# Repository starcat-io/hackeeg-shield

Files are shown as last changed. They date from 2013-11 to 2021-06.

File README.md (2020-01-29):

# HackEEG - ADS1299 Shield

This is an Arduino Due shield for the 
[TI ADS1299 EEG system-on-a-chip](http://www.ti.com/product/ads1299). This is a
system-on-a-chip that includes all commonly-required features for extracranial 
electroencephalogram (EEG) and electrocardiography (ECG) applications.

This board is currently available in the [HackEEG CrowdSupply crowdfunding campaign](https://www.crowdsupply.com/starcat/hackeeg/).
You can buy one or more of the boards by backing the campaign. Here's more about the [HackEEG product](http://starcat.io/hackeeg-shield).

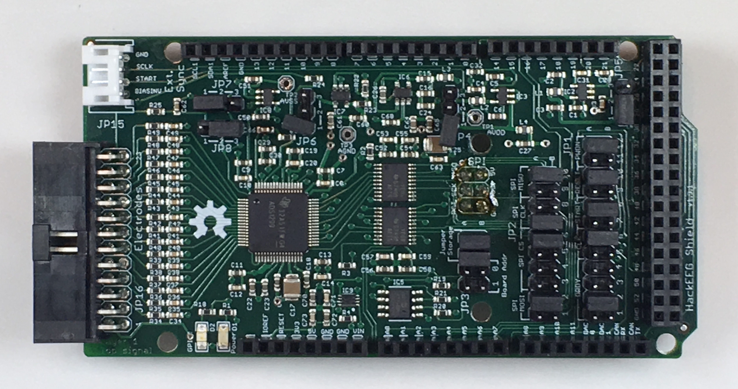
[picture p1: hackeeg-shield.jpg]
Picture of the HackEEG board


This board has been tested, works, and is in use in major research labs in the US and Europe. Design files for two connector boards
are included:

  * connector-8: this has 9 [DIN 42-802](https://en.wikipedia.org/wiki/EEG_DIN_connector) 
    medical electrode connectors (8 single-ended inputs, one ground)
  * connector-12: this has a 12-position screw-terminal connector with 8 single-ended inputs, ground, 
    analog power, digital power, and bias electrode.

I intend to eventually design a case and will post the files here when I do.

I can provide limited support for for individuals. Commercial support is available for corporations.

## Features

* Up to 4 shields can be stacked on one Arduino Due, for a total of 32 EEG channels
* DMA drivers can read and transfer 8 channels of 24-bit resolution data at 16,000 samples per second (Arduino Due only)
* SPI EEPROM for storing configuration data
* Jumpers for configuring most of the data and control lines to the Arduino
* 2 board-stacks can be daisy-chained and clock-synchronized to capture 64 EEG channels (this is experimental)
* Level shifters mean the board is compatible with both the [Arduindo Due](ihttps://store.arduino.cc/usa/due) and 
[Arduino Mega2560](https://store.arduino.cc/usa/mega-2560-r3).
* Single-ended and differential inputs are available on the electrode connector.

## Warning

When used with humans, mammals, or other higher animals, this board is meant to be used **only** in battery powered systems. It has no patient isolation circuitry.
Don't connect it, or any system it is connected to, to mains (wall or AC) power. **Use at your own risk.**

## Documentation

* [Connector Pinouts](https://github.com/starcat-io/hackeeg-shield/blob/master/docs/connectors.md)
* [Configuration Reference](https://github.com/starcat-io/hackeeg-shield/blob/master/docs/configuration.md)
* [Typical Configuration](https://github.com/starcat-io/hackeeg-shield/blob/master/docs/typical-configuration.md)

## Driver Software

The Arduino Due and Mega2560 driver software for this board can be found in the [hackeeg-driver-arduino](https://github.com/starcat-io/hackeeg-driver-arduino) repository.

## License

[CERN Open Hardware License v.1.2](http://ohwr.org/cernohl)

## Comments

If you have questions, comments, or improvements, I would love to know them!

cheers <br>
adam <br>
<br>
Adam Feuer <br>
adam@starcat.io<br>
[Starcat LLC](https://starcat.io)<br>
Seattle, WA, USA <br>

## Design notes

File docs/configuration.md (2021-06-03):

# HackEEG Configuration

These jumpers configure Arduino Due pins used on the HackEEG shield. For commonly-used settings, see [Typical Configuration](https://github.com/adamfeuer/hackeeg-shield/blob/master/docs/typical-configuration.md).

For ADS1299 pin definitions, refer to [ADS1299 datasheet](http://www.ti.com/lit/ds/symlink/ads1299.pdf).

For Arduino Due pin definitions, refer to the [Arduino Due pinout diagram](https://raw.githubusercontent.com/adamfeuer/hackeeg-shield/master/docs/arduino_due_pinout.png), the [Arduino Due reference](https://www.arduino.cc/en/Main/ArduinoBoardDue), and the [SAM3X8E datasheet](http://www.atmel.com/Images/Atmel-11057-32-bit-Cortex-M3-Microcontroller-SAM3X-SAM3A_Datasheet.pdf).

If you change these jumpers, you must also change the pin definitions in your driver files. For the ads129x_tools driver, this is in the file [adsCommand.h](https://github.com/adamfeuer/ADS129x-tools/blob/master/ads129x_driver/adsCommand.h)

## Jumper Diagram

This diagram shows the locations of all the configuration jumpers:

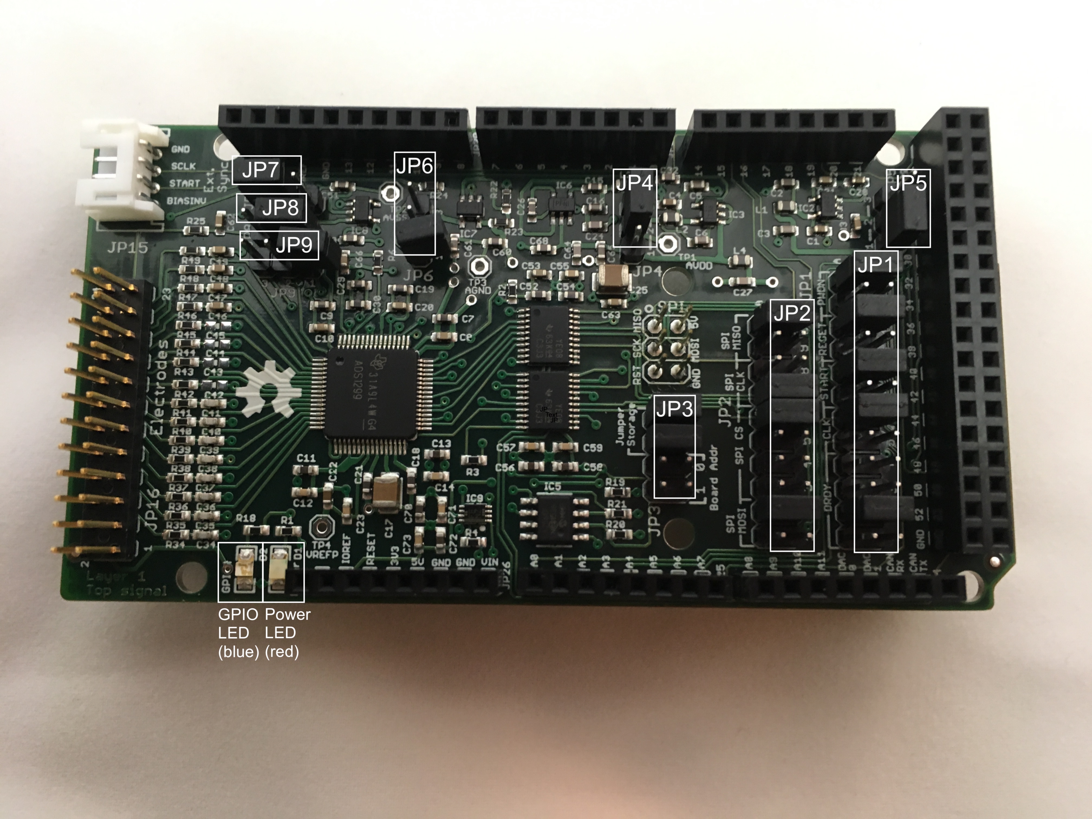
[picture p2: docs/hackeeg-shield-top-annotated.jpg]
Annotated picture of the HackEEG board showing jumper locations


## Digital Configuration Jumpers

### JP1 and JP2 – Board Connection

These pins select which ADS1299 pins are connected to which Arduino Due pins. Bridging one pair of jumpers connects the pins together. This enables a stack of shields to use different Arduino Due pins if needed, for instance to connect two HackEEG shields to the native SPI, and two to the USART1 SPI, or to use different Arduino Due PIO pins to control the ADS1299.

For each named signal, you must set exactly one jumper.
    
#### JP1 – Config0 – ADS1299 Control Configuration

| Signal      | Jumper #    | Arduino pin  |
|------------ |------------ | ------------ |
| `DRDY`      | 1           | D24          |
| `DRDY`      | 2           | D25          |
| `DRDY`      | 3           | D26          |
| `DRDY`      | 4           | D27          |
| `CLK`       | 5           | D30          |
| `CLK`       | 6           | D31          |
| `START`     | 7           | D61          |
| `START`     | 8           | D59          |
| `RESET`     | 9           | D46          |
| `RESET`     | 10          | D47          |
| `PWDN`      | 11          | D32          |
| `PWDN`      | 12          | D33          |

#### JP2 – Config1 – SPI Configuration

| Signal       | Port           | Jumper # | Arduino pin |
|------------  | -------------- | -------- |------------ |
| `SPI MOSI`   | Native         | 1        | SPI4        |
| `SPI MOSI`   | USART1         | 2        | D16         |
| `SPI CS`     | Chip Select    | 3        | D23         |
| `SPI CS`     | Chip Select    | 4        | D52         |
| `SPI CS`     | Chip Select    | 5        | D10         |
| `SPI CS`     | Chip Select    | 6        | D4          |
| `SPI SCL`    | Native         | 7        | SPI3        |
| `SPI SCL`    | USART1         | 8        | A0          |
| `SPI MISO`   | Native         | 9        | SPI1        |
| `SPI MISO`   | USART1         | 10       | D17         |

### Not configurable

These pins are hard-wired and cannot be configured.

| Signal      |Arduino pin        |
|------------ |------------------ |
| `CLKSEL`    | D48               |
| BOARD LED   | ADS1299 `GPIO4`   |

### JP3 – Board Address 

These pins set the 24AA256 I2S EEPROM address 0-3 in binary – they are not connected to Arduino Due pins. The pins are shared with the ADS1299 GPIO, and so can also used as the board address and read via the ADS1299. If not using them as jumpers, external devices can be connected to the header to provide access to the ADS1299 GPIO pins; this usage generally will conflict with using the I2S EEPROM.

| Jumper #   | Function          |
|----------- |------------------ |
| 0          | ADS1299 `GPIO0`   |
| 1          | ADS1299 `GPIO1`   |

## Analog Configuration Jumpers

### Instrumentation Power Supplies

These jumpers configure the instrumentation power supplies that supply the reference voltages for the ADS1299. You can set the ADS1299 to measure voltages in the 0–5V range (unipolar) or in the -2.5V – +2.5V range (bipolar). Bipolar is most commonly used for human or mammal subjects. You must bridge exactly one set of pins on each jumper.

#### JP 4

| Pins        | Function              |
|------------ |---------------------- |
| 1-2         | Sets `AVDD` to 5V     |
| 2-3         | Sets `AVDD` to 2.5V   |
 
#### JP 5

| Pins        | Function                  |
|------------ |-------------------------  |
| 1-2         | Sets `AVSS` to -2.5V      |
| 2-3         | Sets `AVDD` to `GROUND`   |

#### Common Settings

| Mode Name | ADS1299 Voltage Range    | JP4 Pins| JP5 Pins |
|---------- |------------------------- |---------|--------- |
| Unipolar  | 0–5V                     | 1-2     | 2-3      |
| Bipolar   | -2.5V – +2.5V            | 2-3     | 1-2      |

### Stimulus-Response Buffer (SRB)

#### JP6 – SRB1 - BIAS

| Pins              | Function                                                                              |
|---------------    |-------------------------------------------------------------------------------------- |
| 1-2               | Routes `SRB1` to `BIAS_ELEC` on the electrode connector via a 5K resistor             |
| 2-3               | Routes a noise source to `SRB1`                                                       |
| Unconnected       | Disconnects `BIAS` from `SRB1` – use in conjunction with JP7/JP8 `REF_ELEC` functions |

Setting pins 2-3 can be used to test channel noise performance. See section 8.3 of the [TI EEG Front-End Demonstration Kit manual](http://www.ti.com/lit/ug/slau443b/slau443b.pdf). In this mode, `BIAS_ELEC` and `REF_ELEC` on the electrode connector need to be connected with a cable, since there is no jumper to do so on the HackEEG board.

#### JP7 – SRB1–REF_ELEC 

| Pins          | Function                                                                 |
|------------   |------------------------------------------------------------------------- |
| 1-2           | Routes `SRB1` to `REF_ELEC` on the electrode connector via a 5K resistor |
| 2-3           | Routes `SRB2` to `SRB1` via an opamp                                     |

#### JP8 – SRB2–REF_ELEC 

| Pins          | Function                                                                          |
|------------   |---------------------------------------------------------------------------------- |
| 1-2           | Routes `REF_ELEC` on the electrode connector to the opamp input via a 5K resistor |
| 2-3           | Routes `SRB2` to the opamp input                                                  |

#### JP9 – BIASIN-BIASOUT-BIAS_ELEC 

| Pins          | Function                                                                       |
|------------   |------------------------------------------------------------------------------- |
| 1-2           | Routes `BIASOUT` to `BIAS_ELEC` on the electrode connector via a 5K resistor   |
| 2-3           | Routes `BIASOUT` to `BIASIN`                                                   |
| Unconnected   | Leaves `BIASOUT`, `BIASIN`, and `BIAS_ELEC` unconnected                        |

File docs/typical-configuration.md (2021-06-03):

# HackEEG Typical Configuration

The HackEEG comes from the factory configured this way and the drivers are set up to use it.

## Jumper Diagram

This diagram shows the locations of all the configuration jumpers:

Annotated picture of the HackEEG board showing jumper locations

## Digital Configuration Jumpers

### JP1 and JP2 – Board Connection
    
#### JP1 – Config0 – ADS1299 Control Configuration

| Signal      | Jumper #  | Arduino pin |
|------------ |---------- |------------ |
| `DRDY`      | 2         | D25         |
| `CLK`       | 6         | D31         |
| `START`     | 7         | D61         |
| `START`     | 8         | D59         |
| `RESET`     | 10        | D47         |
| `PWDN`      | 12        | D33         |

#### JP2 – Config1 – SPI Configuration

| Signal      | Port           |Jumper # | Arduino pin |
|------------ |--------------- |-------- |------------ |
| `SPI MOSI`  | Native         | 1       | SPI4        |
| `SPI CS`    | Chip Select    | 6       | D23         |
| `SPI SCL`   | Native         | 7       | SPI3        |
| `SPI MISO`  | Native         | 9       | SPI1        |

### Not configurable

These pins are hard-wired and cannot be configured.

| Signal      |Arduino pin        |
|------------ |------------------ |
| `CLKSEL`    | D48               |
| BOARD LED   | ADS1299 `GPIO4`   |

### JP3 – Board Address 

No jumpers set, so board address is 0.

## Analog Configuration Jumpers

### Instrumentation Power Supplies

The HackEEG comes configured in bipolar mode:

| Mode Name | ADS1299 Voltage Range    | JP4 Pins| JP5 Pins |
|---------- |------------------------- |---------|--------- |
| Bipolar   | -2.5V – +2.5V            | 2-3     | 1-2      |

#### JP 4

| Pins        | Function              |
|------------ |---------------------- |
| 2-3         | Sets `AVDD` to 2.5V   |
 
#### JP 5

| Pins        | Function                 |
|------------ |------------------------- |
| 1-2         | Sets `AVSS` to -2.5V     |

### Stimulus-Response Buffer (SRB)

#### JP6 – SRB1 - BIAS

| Pins           | Function                                                                              |
|--------------- |-------------------------------------------------------------------------------------- |
| Unconnected    | Disconnects `BIAS` from `SRB1` – use in conjunction with JP7/JP8 `REF_ELEC` functions |

#### JP7 – SRB2–REF_ELEC 

| Pins        | Function                                                             |
|------------ |--------------------------------------------------------------------- |
| Unconnected | Routes `REF_ELEC` on the electrode connector via a 5K resistor       |

#### JP8 – SRB1–REF_ELEC 

| Pins       | Function                                                                  |
|----------- | ------------------------------------------------------------------------- |
| 1-2        | Routes `SRB1` to `REF_ELEC` on the electrode connector via a 5K resistor  |

#### JP9 – BIASIN-BIASOUT-BIAS_ELEC 

| Pins          | Function                                                                       |
|------------   |------------------------------------------------------------------------------- |
| Unconnected   | Leaves `BIASOUT`, `BIASIN`, and `BIAS_ELEC` unconnected                        |

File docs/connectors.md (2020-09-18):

# HackEEG Connector Pinouts

## Electrode Connector

**JP16** is the electrode connector.

### Electrode connector pinout:

|Pin #	|Function						|
|-----	|-------------------------	|
|  1	|`DVDD`						|
|  2	|`AVDD`						|
|  3	|`BIASINV`					|
|  4	| Reserved for Future Use	|
|  5	|`AGND`						|
|  6	|`AGND`						|
|  7	|`IN1P`						|
|  8	|`IN1N`						|
|  9	|`IN2P`						|
| 10	|`IN2N`						|
| 11	|`IN3P`						|
| 12	|`IN3N`						|
| 13	|`IN4P`						|
| 14	|`IN4N`						|
| 15	|`IN5P`						|
| 16	|`IN5N`						|
| 17	|`IN6P`						|
| 18	|`IN6N`						|
| 19	|`IN7P`						|
| 20	|`IN7N`						|
| 21	|`IN8P`						|
| 22	|`IN8N`						|
| 23	|`REF_ELEC_CONN`				|
| 24	|`BIAS_ELEC_CONN`			|

Looking at the pins edge on (not from above), this is the pinout diagram:

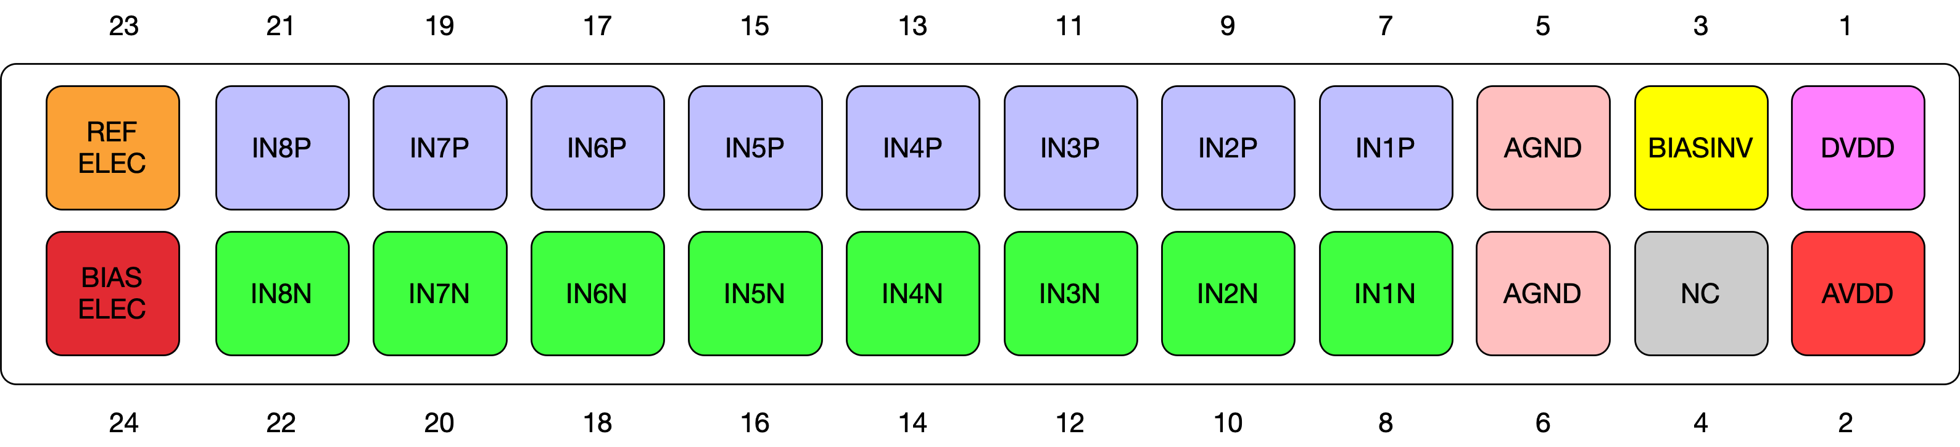
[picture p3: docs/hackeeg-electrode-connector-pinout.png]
HackEEG Electrode Connector pinout diagram


## External Sync connector

This connector is experimental, and not supported at this time. You can enable it using the various ADS1299 register settings.

### External Sync connector pinout

|Pin #	|Function			|
|-----	|---------------	|
| 1   	|`BIASINV`		|
| 2   	|`ADS_START`   	|
| 3  	|`ADS_SPI_CLK`	|
| 4  	|`AGND`   		|

## Checking the connector pinouts against the schematic

If you want to check the pinout, you can see the connectors on the schematic on sheet 2:

[HackEEG Shield schematic](https://github.com/adamfeuer/hackeeg-shield/blob/master/hackeeg-shield.pdf)

## Making cables

### Electrode Connector cables

**JP16** is the large, black male 24-pin shrouded electrode connector that is soldered on the board: [On Shore Technology 24-pin right angle male shrouded header](https://www.digikey.com/product-detail/en/on-shore-technology-inc/101-246/ED10537-ND)

This the mating female connector that I use to construct ribbon cables to connect the connector boards with the HackEEG shield:

[On Shore Technologies 	101-246 IDC socket connector for ribbon cable](https://www.digikey.com/product-detail/en/on-shore-technology-inc/101-246/ED10504-ND)

Here's the ribbon cable I used:

[24-conductor ribbon cable, 5 foot length](https://www.digikey.com/product-detail/en/3m/3365-24-300SF/MC24G-5-ND/)

You'll need a tool to crimp them, I used this one from Amazon:

[IDC crimp tool](https://www.amazon.com/gp/product/B007R2JEM4)

Alternatively, any 24-pin female header with receptacles on 0.1" centers should work if you want to use one and solder some wires to it.

### External Sync Connector cables

**JP15** is the small, white male 4-pin shrouded connector that is used for synchronizing the ADS1299 with another board.

This is the connector that is soldered on the board: [JST 4-pin Shrouded Male Header ](http://www.digikey.com/product-detail/en/S4B-PH-K-S(LF)(SN)/455-1721-ND/926628)

Here is the [Mating JST connector](http://www.digikey.com/product-detail/en/PHR-4/455-1164-ND/608606) and [Crimp Contact that fits the housing](http://www.digikey.com/product-detail/en/SPH-004T-P0.5S/455-1318-1-ND/608807) - these can be crimped with this tool:

[HT-225D Full Cycle Ratchet Crimping Tool with interchangeable die set HT-225D](http://www.amazon.com/dp/B007JLN93S)

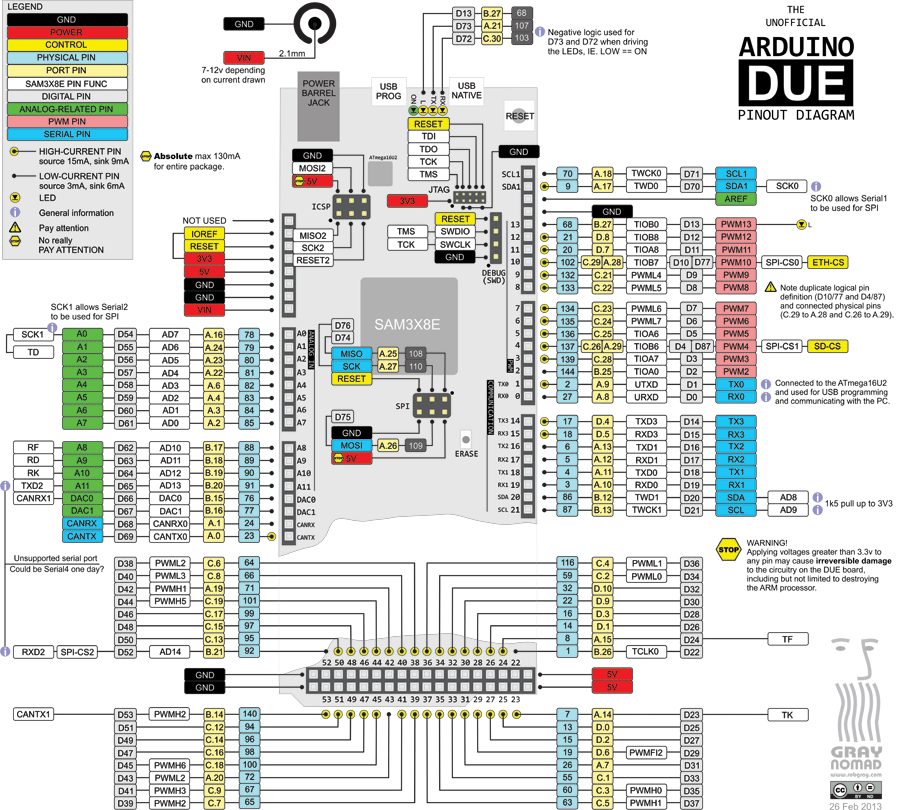
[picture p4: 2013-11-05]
docs/arduino_due_pinout.png

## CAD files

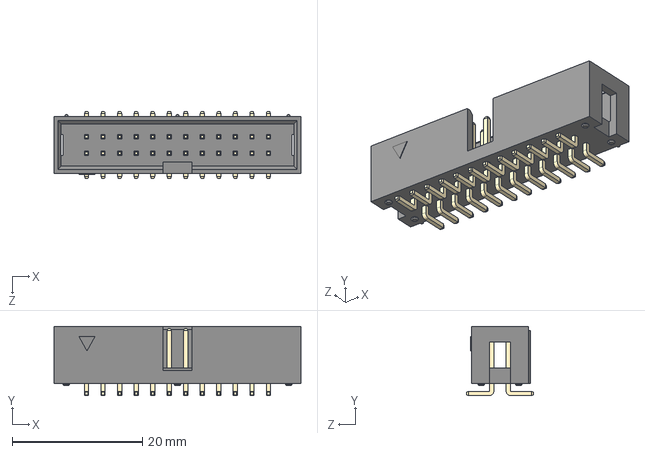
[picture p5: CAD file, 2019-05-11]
models/SBH11-NBPC-D12-SM-BK--3DModel-STEP-56544.STEP
38.0 x 10.6 x 10.3 mm

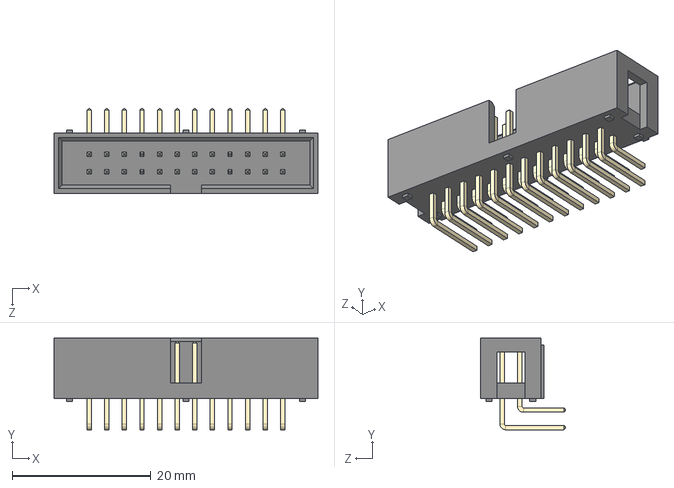
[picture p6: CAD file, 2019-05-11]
models/302-R241--3DModel-STEP-56544.STEP
38.1 x 13.2 x 12.2 mm

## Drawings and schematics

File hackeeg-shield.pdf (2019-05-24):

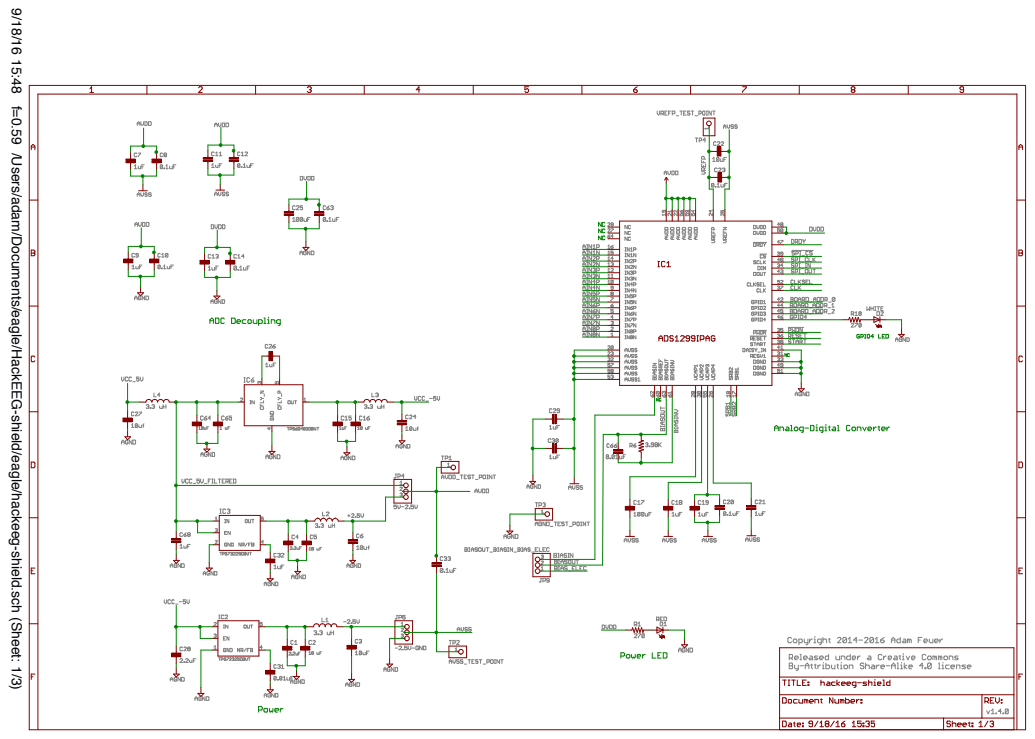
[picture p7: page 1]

9/18/16 15:48 f=0.59 /Users/adam/Documents/eagle/HackEEG-shield/eagle/hackeeg-shield.sch (Sheet: 1/3)

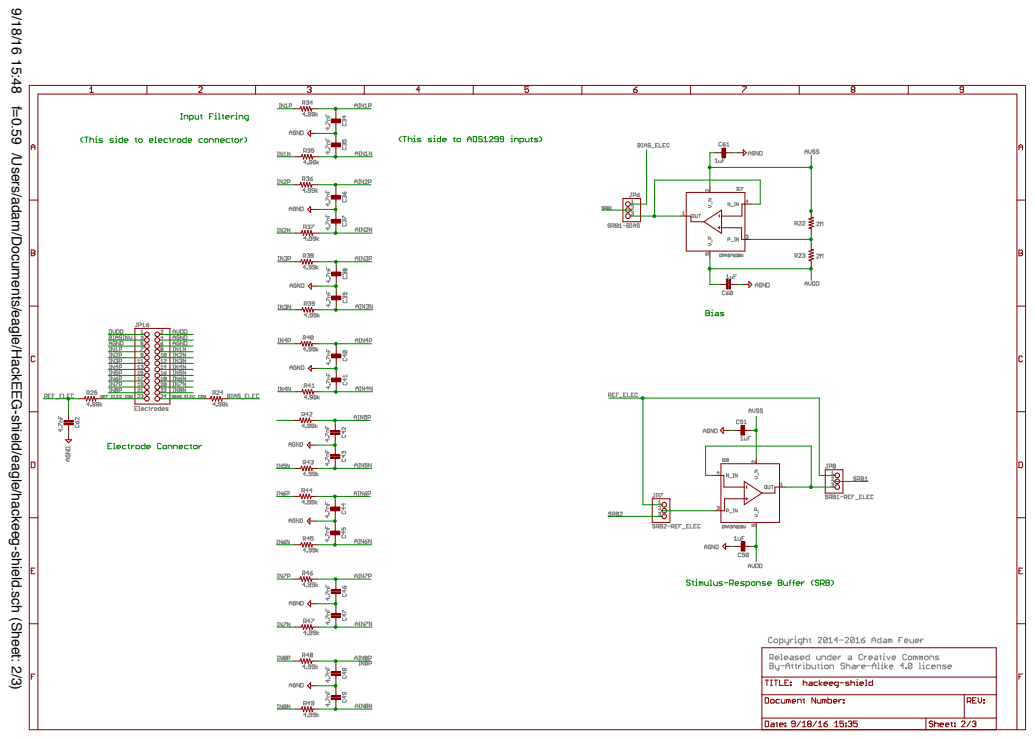
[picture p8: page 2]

9/18/16 15:48 f=0.59 /Users/adam/Documents/eagle/HackEEG-shield/eagle/hackeeg-shield.sch (Sheet: 2/3)

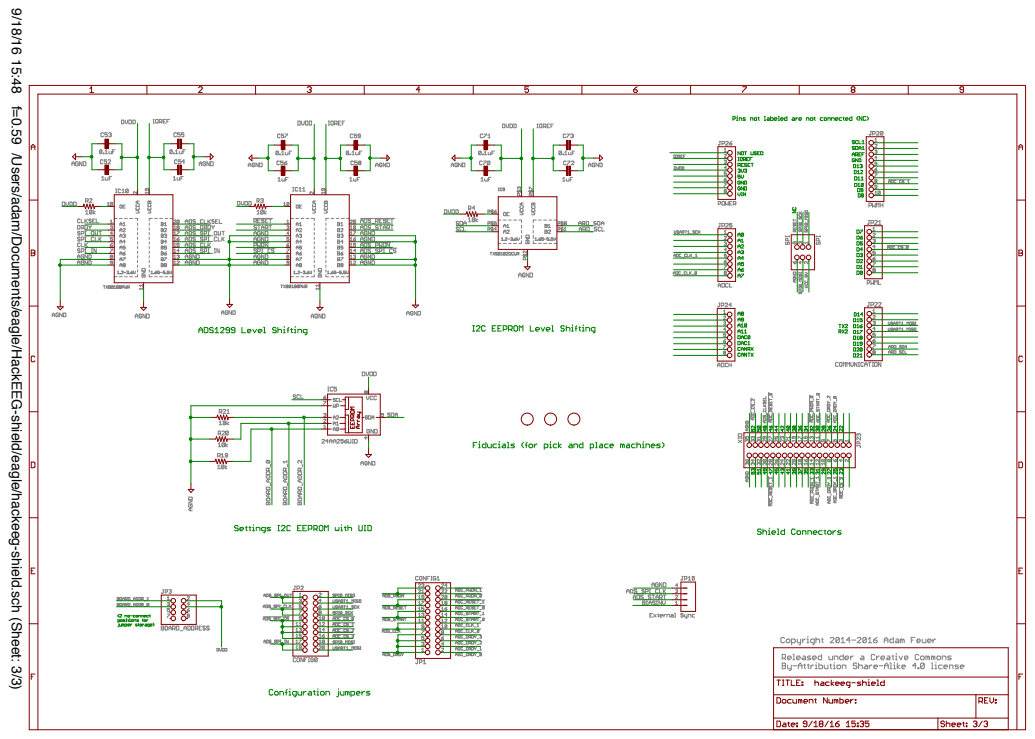
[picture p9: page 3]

9/18/16 15:48 f=0.59 /Users/adam/Documents/eagle/HackEEG-shield/eagle/hackeeg-shield.sch (Sheet: 3/3)

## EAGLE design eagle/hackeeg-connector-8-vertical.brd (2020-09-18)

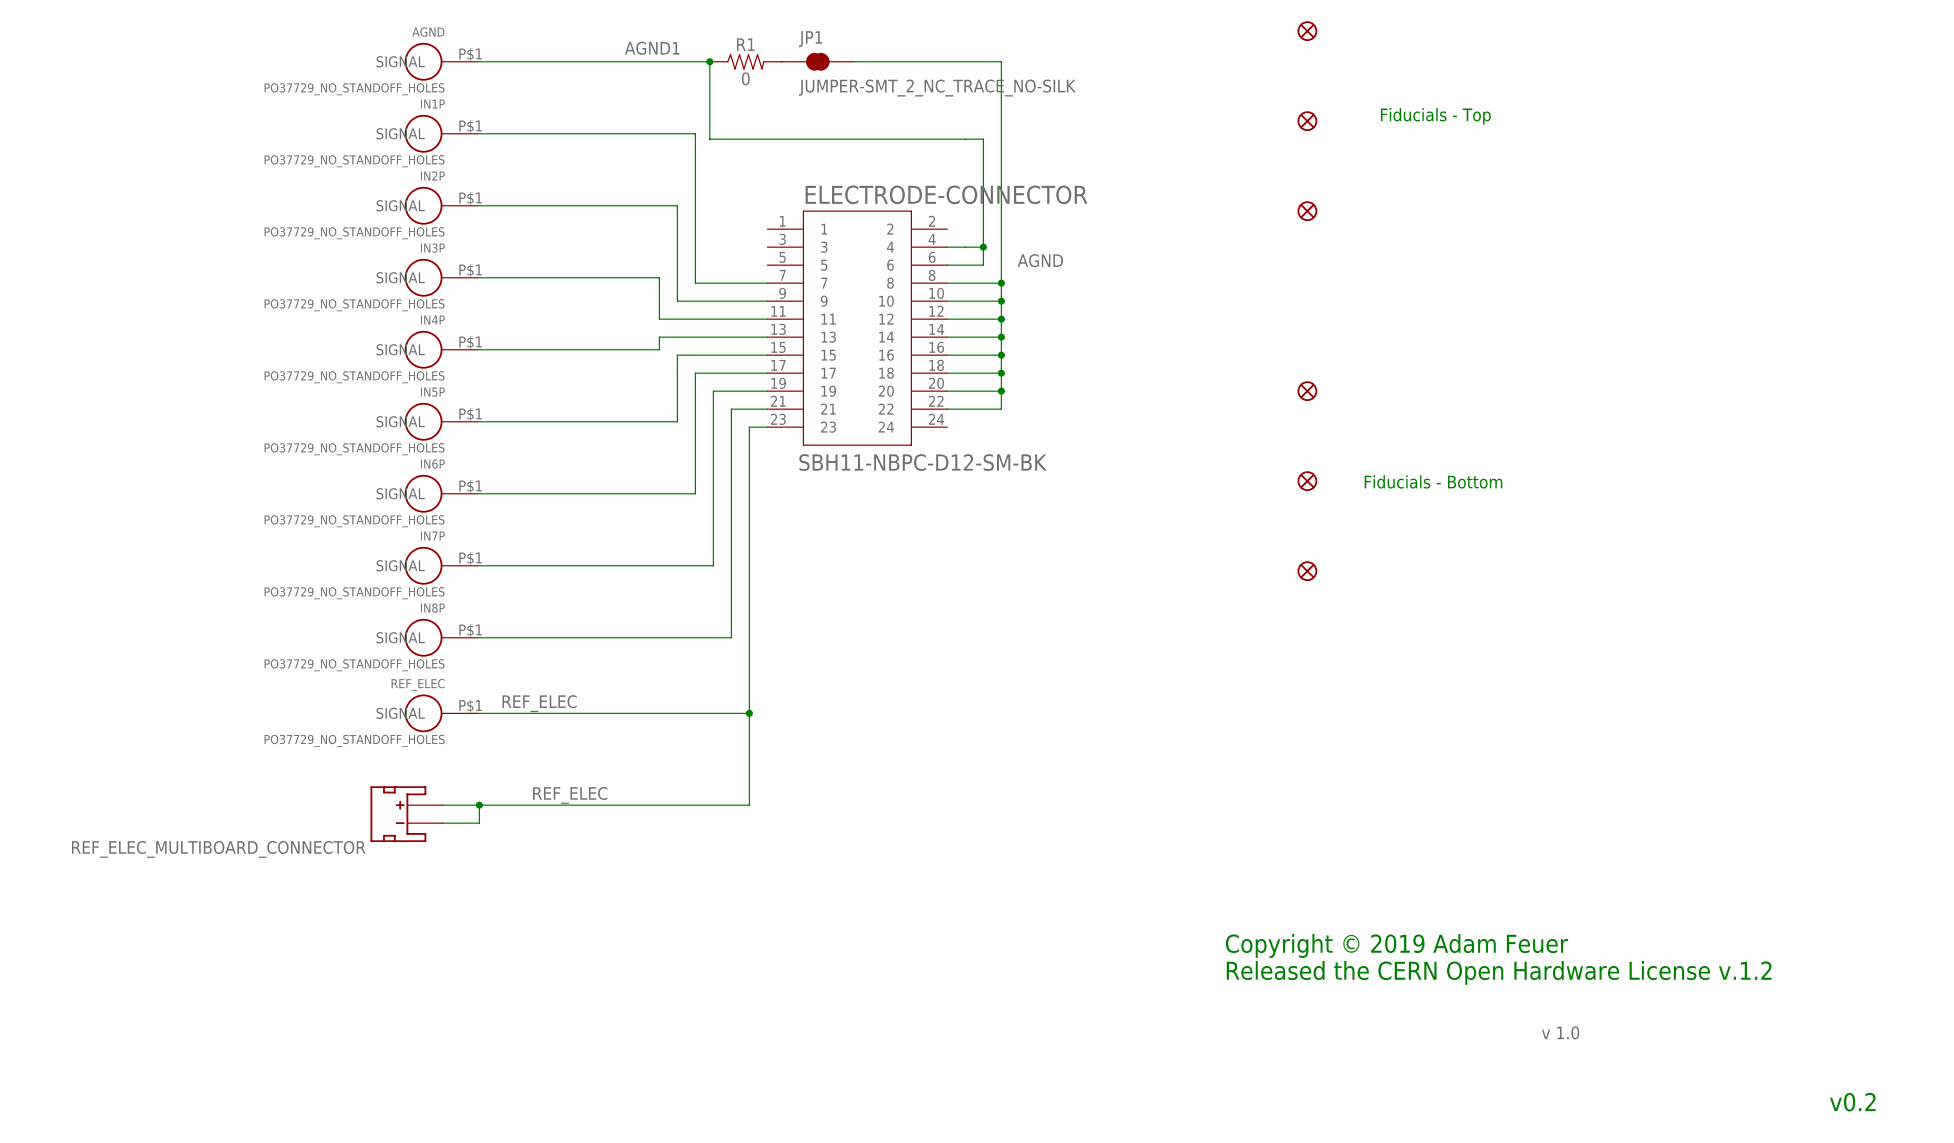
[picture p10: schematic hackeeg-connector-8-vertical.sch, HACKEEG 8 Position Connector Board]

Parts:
AGND: PO37729_NO_STANDOFF_HOLES; SIMPLE0
ELECTRODE-CONNECTOR: SBH11-NBPC-D12-SM-BK; SULLINS_SBH11-NBPC-D12-SM-BK
FD1, FD2, FD3, FD4, FD5, FD6: FIDUCIAL1X2; FIDUCIAL-1X2
IN1P, IN2P, IN3P, IN4P, IN5P, IN6P, IN7P, IN8P: PO37729_NO_STANDOFF_HOLES; SIMPLE0
JP1: JUMPER-SMT_2_NC_TRACE_NO-SILK; SMT-JUMPER_2_NC_TRACE_NO-SILK
R1: 0; 0603
REF_ELEC: PO37729_NO_STANDOFF_HOLES; SIMPLE0
REF_ELEC_MULTIBOARD_CONNECTOR: JST_2MM_MALE; JST-2-SMD

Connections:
AGND: ELECTRODE-CONNECTOR.8, ELECTRODE-CONNECTOR.10, ELECTRODE-CONNECTOR.12, ELECTRODE-CONNECTOR.14, ELECTRODE-CONNECTOR.16, ELECTRODE-CONNECTOR.18, ELECTRODE-CONNECTOR.20, ELECTRODE-CONNECTOR.22, JP1.2
AGND1: AGND.P$1, ELECTRODE-CONNECTOR.4, ELECTRODE-CONNECTOR.6, R1.1
unnamed: ELECTRODE-CONNECTOR.7, IN1P.P$1
unnamed: ELECTRODE-CONNECTOR.9, IN2P.P$1
unnamed: ELECTRODE-CONNECTOR.11, IN3P.P$1
unnamed: ELECTRODE-CONNECTOR.13, IN4P.P$1
unnamed: ELECTRODE-CONNECTOR.15, IN5P.P$1
unnamed: ELECTRODE-CONNECTOR.17, IN6P.P$1
unnamed: ELECTRODE-CONNECTOR.19, IN7P.P$1
unnamed: ELECTRODE-CONNECTOR.21, IN8P.P$1
unnamed: JP1.1, R1.2
REF_ELEC: ELECTRODE-CONNECTOR.23, REF_ELEC.P$1, REF_ELEC_MULTIBOARD_CONNECTOR.1 (-), REF_ELEC_MULTIBOARD_CONNECTOR.2 (+)

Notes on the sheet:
Fiducials - Top
Fiducials - Bottom
v 1.0
v0.2
Copyright © 2019 Adam Feuer Released the CERN Open Hardware License v.1.2

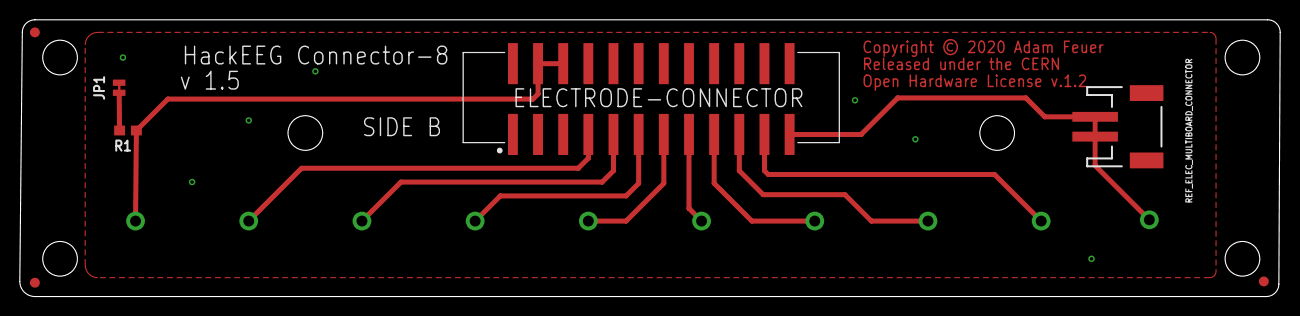
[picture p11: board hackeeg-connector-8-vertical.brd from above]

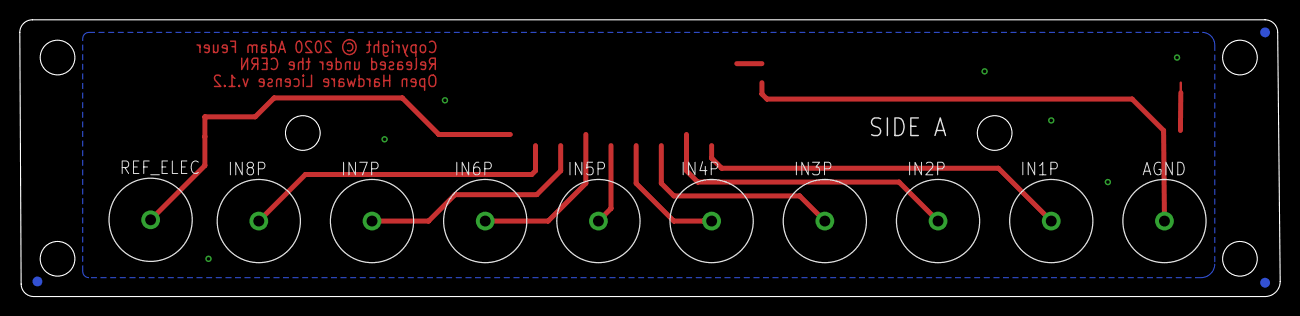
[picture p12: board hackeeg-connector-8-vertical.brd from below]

Board: 2 copper layers, 127.3 x 27.9 mm, 20 parts (13 on the bottom side), 12 nets.

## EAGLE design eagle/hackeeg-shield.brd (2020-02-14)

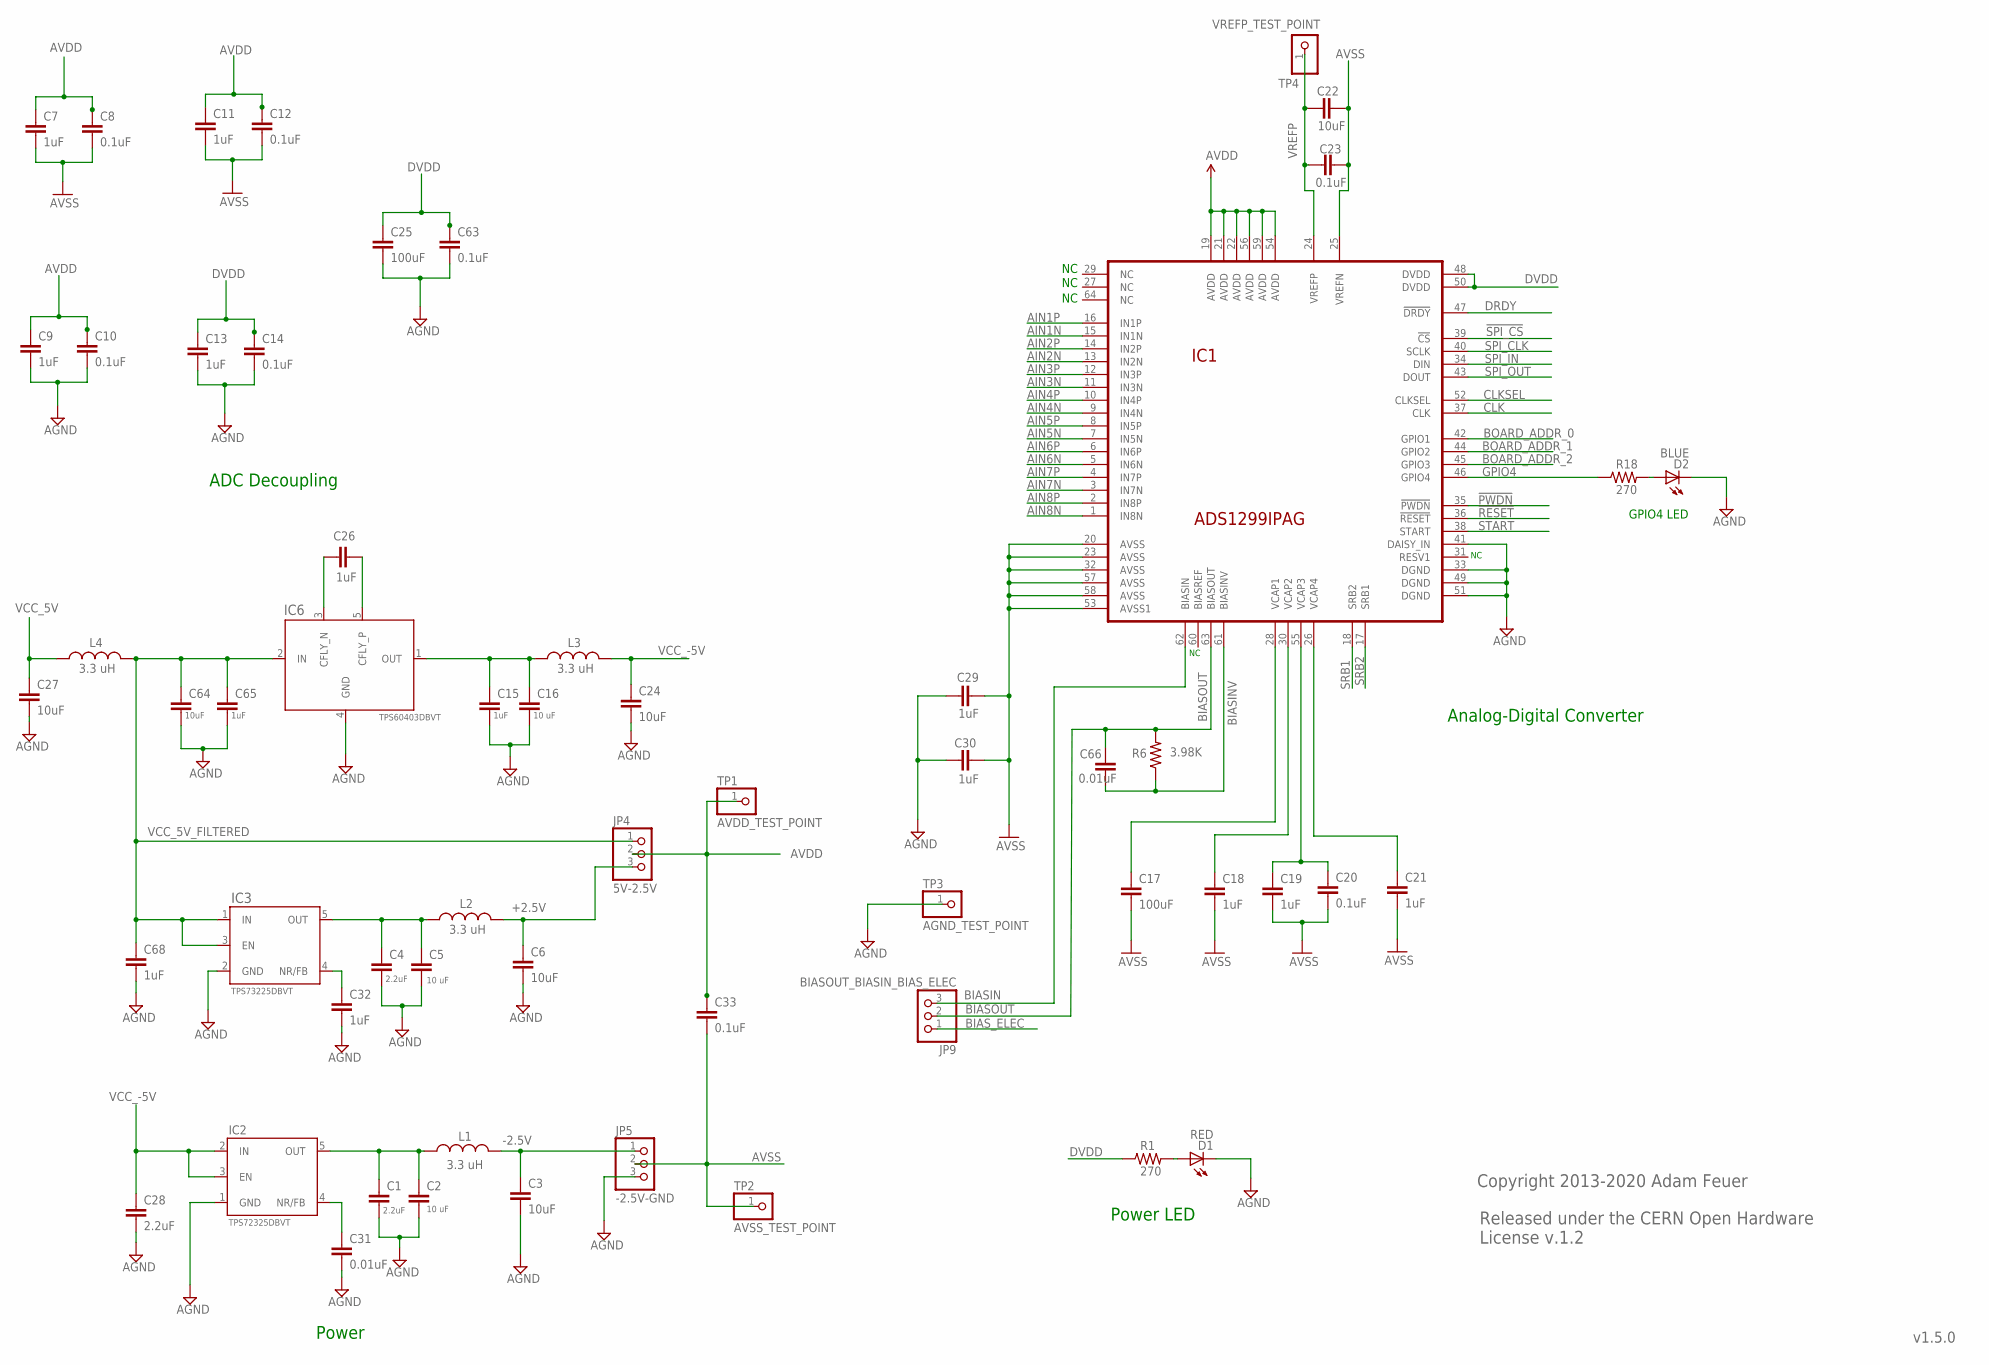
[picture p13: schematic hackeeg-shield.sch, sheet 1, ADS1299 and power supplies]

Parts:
C1, C4, C28: 2.2uF; 0603-CAP
C2, C5, C16: 10 uF; 0603-CAP
C3, C6, C22, C24, C27, C64: 10uF; 0603-CAP
C7, C9, C11, C13, C15, C18, C19, C21, C26, C29, C30, C32, C65, C68: 1uF; 0603-CAP
C8, C10, C12, C14, C20, C23, C33, C63: 0.1uF; 0603-CAP
C17, C25: 100uF; 1210
C31, C66: 0.01uF; 0603-CAP
D1: RED; LED-1206
D2: BLUE; LED-1206
IC1: ADS1299IPAG; TQFP64
IC2: TPS72325DBVT; SOT23-5
IC3: TPS73225DBVT; SOT23-5
IC6: TPS60403DBVT; SOT23-5
JP4: 5V-2.5V; 1X03
JP5: -2.5V-GND; 1X03
JP9: BIASOUT_BIASIN_BIAS_ELEC; 1X03
L1, L2, L3, L4: 3.3 uH; 0805
R1, R18: 270; 0603-RES
R6: 3.98K; 0603-RES
TP1: AVDD_TEST_POINT; 1X01
TP2: AVSS_TEST_POINT; 1X01
TP3: AGND_TEST_POINT; 1X01
TP4: VREFP_TEST_POINT; 1X01

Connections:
!PWDN: IC1.35 (!PWDN); also elsewhere on the board
!RESET: IC1.36 (!RESET); also elsewhere on the board
!SPI_CS: IC1.39 (!CS); also elsewhere on the board
+2.5V: C6.1, JP4.3, L2.2
-2.5V: C3.1, JP5.1, L1.2
AGND: C1.2, C2.2, C3.2, C4.2, C5.2, C6.2, C9.2, C10.2, C13.2, C14.2, C15.2, C16.2, C24.2, C25.2, C27.2, C28.2, C29.1, C30.1, C31.2, C32.2, C63.2, C64.2, C65.2, C68.2, D1.C, D2.C, IC1.33 (DGND), IC1.41 (DAISY_IN), IC1.49 (DGND), IC1.51 (DGND), IC2.1 (GND), IC3.2 (GND), IC6.4 (GND), JP5.3, TP3.1; also elsewhere on the board
AIN1N: IC1.15 (IN1N); also elsewhere on the board
AIN1P: IC1.16 (IN1P); also elsewhere on the board
AIN2N: IC1.13 (IN2N); also elsewhere on the board
AIN2P: IC1.14 (IN2P); also elsewhere on the board
AIN3N: IC1.11 (IN3N); also elsewhere on the board
AIN3P: IC1.12 (IN3P); also elsewhere on the board
AIN4N: IC1.9 (IN4N); also elsewhere on the board
AIN4P: IC1.10 (IN4P); also elsewhere on the board
AIN5N: IC1.7 (IN5N); also elsewhere on the board
AIN5P: IC1.8 (IN5P); also elsewhere on the board
AIN6N: IC1.5 (IN6N); also elsewhere on the board
AIN6P: IC1.6 (IN6P); also elsewhere on the board
AIN7N: IC1.3 (IN7N); also elsewhere on the board
AIN7P: IC1.4 (IN7P); also elsewhere on the board
AIN8N: IC1.1 (IN8N); also elsewhere on the board
AIN8P: IC1.2 (IN8P); also elsewhere on the board
AVDD: C7.1, C8.1, C9.1, C10.1, C11.1, C12.1, C33.1, IC1.19 (AVDD), IC1.21 (AVDD), IC1.22 (AVDD), IC1.54 (AVDD), IC1.56 (AVDD), IC1.59 (AVDD), JP4.2, TP1.1; also elsewhere on the board
AVSS: C7.2, C8.2, C11.2, C12.2, C17.2, C18.2, C19.2, C20.2, C21.2, C22.2, C23.2, C29.2, C30.2, C33.2, IC1.20 (AVSS), IC1.23 (AVSS), IC1.25 (VREFN), IC1.32 (AVSS), IC1.53 (AVSS1), IC1.57 (AVSS), IC1.58 (AVSS), JP5.2, TP2.1; also elsewhere on the board
BIASIN: IC1.62 (BIASIN), JP9.3
BIASINV: C66.2, IC1.61 (BIASINV), R6.1; also elsewhere on the board
BIASOUT: C66.1, IC1.63 (BIASOUT), JP9.2, R6.2
BIAS_ELEC: JP9.1; also elsewhere on the board
BOARD_ADDR_0: IC1.42 (GPIO1); also elsewhere on the board
BOARD_ADDR_1: IC1.44 (GPIO2); also elsewhere on the board
BOARD_ADDR_2: IC1.45 (GPIO3); also elsewhere on the board
CLK: IC1.37 (CLK); also elsewhere on the board
CLKSEL: IC1.52 (CLKSEL); also elsewhere on the board
DRDY: IC1.47 (!DRDY); also elsewhere on the board
DVDD: C13.1, C14.1, C25.1, C63.1, IC1.48 (DVDD), IC1.50 (DVDD), R1.1; also elsewhere on the board
GPIO4: IC1.46 (GPIO4), R18.1
unnamed: C4.1, C5.1, IC3.5 (OUT), L2.1
unnamed: C1.1, C2.1, IC2.5 (OUT), L1.1
unnamed: C17.1, IC1.28 (VCAP1)
unnamed: C18.1, IC1.30 (VCAP2)
unnamed: C19.1, C20.1, IC1.55 (VCAP3)
unnamed: C15.1, C16.1, IC6.1 (OUT), L3.1
unnamed: C21.1, IC1.26 (VCAP4)
unnamed: C26.2, IC6.5 (CFLY_P)
unnamed: C26.1, IC6.3 (CFLY_N)
unnamed: C32.1, IC3.4 (NR/FB)
unnamed: C31.1, IC2.4 (NR/FB)
unnamed: D2.A, R18.2
unnamed: D1.A, R1.2
SPI_CLK: IC1.40 (SCLK); also elsewhere on the board
SPI_IN: IC1.34 (DIN); also elsewhere on the board
SPI_OUT: IC1.43 (DOUT); also elsewhere on the board
SRB1: IC1.18 (SRB2); also elsewhere on the board
SRB2: IC1.17 (SRB1); also elsewhere on the board
START: IC1.38 (START); also elsewhere on the board
VCC_5V: C27.1, L4.1; also elsewhere on the board
VCC_5V_FILTERED: C64.1, C65.1, C68.1, IC3.1 (IN), IC3.3 (EN), IC6.2 (IN), JP4.1, L4.2
VCC_-5V: C24.1, C28.1, IC2.2 (IN), IC2.3 (EN), L3.2
VREFP: C22.1, C23.1, IC1.24 (VREFP), TP4.1

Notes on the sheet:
Released under the CERN Open Hardware License v.1.2
Copyright 2013-2020 Adam Feuer
v1.5.0
ADC Decoupling
Power
Analog-Digital Converter
GPIO4 LED
Power LED

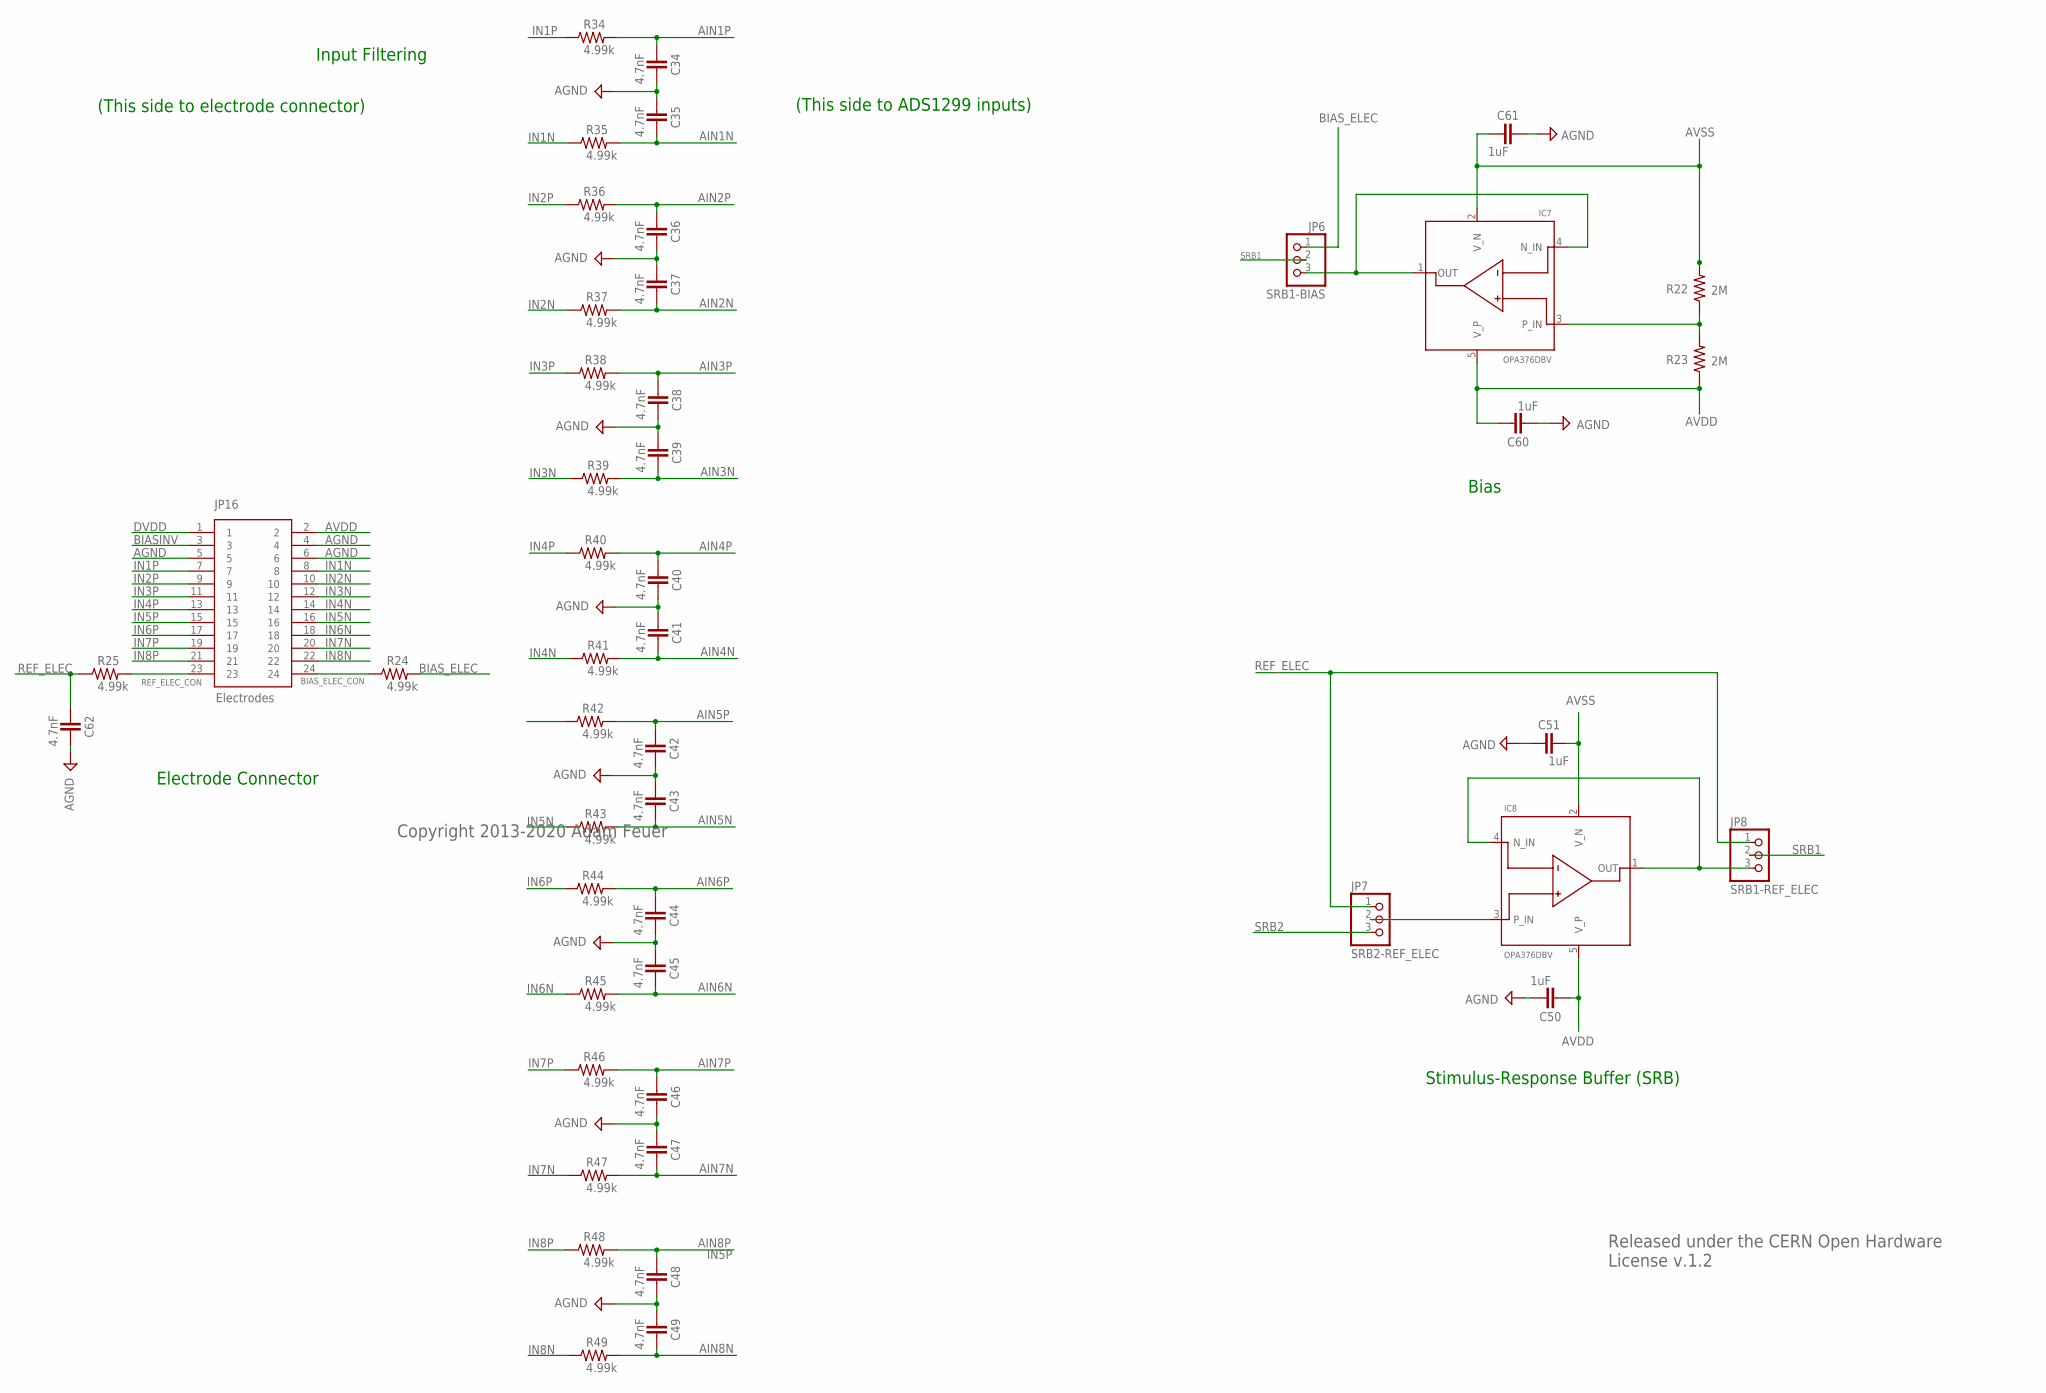
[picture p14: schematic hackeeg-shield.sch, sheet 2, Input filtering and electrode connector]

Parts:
C34, C35, C36, C37, C38, C39, C40, C41, C42, C43, C44, C45, C46, C47, C48, C49, C62: 4.7nF; 0603-CAP
C50, C51, C60, C61: 1uF; 0603-CAP
IC7, IC8: OPA376DBV; SOT23-5
JP6: SRB1-BIAS; 1X03
JP7: SRB2-REF_ELEC; 1X03
JP8: SRB1-REF_ELEC; 1X03
JP16: Electrodes; OST_302-R241
R22, R23: 2M; 0603-RES
R24, R25, R34, R35, R36, R37, R38, R39, R40, R41, R42, R43, R44, R45, R46, R47, R48, R49: 4.99k; 0603-RES

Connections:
AGND: C34.2, C35.1, C36.2, C37.1, C38.2, C39.1, C40.2, C41.1, C42.2, C43.1, C44.2, C45.1, C46.2, C47.1, C48.2, C49.1, C50.2, C51.1, C60.2, C61.1, C62.2, JP16.4, JP16.5, JP16.6; also elsewhere on the board
AIN1N: C35.2, R35.2; also elsewhere on the board
AIN1P: C34.1, R34.2; also elsewhere on the board
AIN2N: C37.2, R37.2; also elsewhere on the board
AIN2P: C36.1, R36.2; also elsewhere on the board
AIN3N: C39.2, R39.2; also elsewhere on the board
AIN3P: C38.1, R38.2; also elsewhere on the board
AIN4N: C41.2, R41.2; also elsewhere on the board
AIN4P: C40.1, R40.2; also elsewhere on the board
AIN5N: C43.2, R43.2; also elsewhere on the board
AIN5P: C42.1, R42.2; also elsewhere on the board
AIN6N: C45.2, R45.2; also elsewhere on the board
AIN6P: C44.1, R44.2; also elsewhere on the board
AIN7N: C47.2, R47.2; also elsewhere on the board
AIN7P: C46.1, R46.2; also elsewhere on the board
AIN8N: C49.2, R49.2; also elsewhere on the board
AIN8P: C48.1, R48.2; also elsewhere on the board
AVDD: C50.1, C60.1, IC7.5 (V_P), IC8.5 (V_P), JP16.2, R23.1; also elsewhere on the board
AVSS: C51.2, C61.2, IC7.2 (V_N), IC8.2 (V_N), R22.2; also elsewhere on the board
BIASINV: JP16.3; also elsewhere on the board
BIAS_ELEC: JP6.1, R24.2; also elsewhere on the board
BIAS_ELEC_CON: JP16.24, R24.1
DVDD: JP16.1; also elsewhere on the board
IN1N: JP16.8, R35.1
IN1P: JP16.7, R34.1
IN2N: JP16.10, R37.1
IN2P: JP16.9, R36.1
IN3N: JP16.12, R39.1
IN3P: JP16.11, R38.1
IN4N: JP16.14, R41.1
IN4P: JP16.13, R40.1
IN5N: JP16.16, R43.1
IN5P: JP16.15, R42.1
IN6N: JP16.18, R45.1
IN6P: JP16.17, R44.1
IN7N: JP16.20, R47.1
IN7P: JP16.19, R46.1
IN8N: JP16.22, R49.1
IN8P: JP16.21, R48.1
unnamed: IC7.3 (P_IN), R22.1, R23.2
unnamed: IC8.3 (P_IN), JP7.2
unnamed: IC8.1 (OUT), IC8.4 (N_IN), JP8.3
unnamed: IC7.1 (OUT), IC7.4 (N_IN), JP6.3
REF_ELEC: C62.1, JP7.1, JP8.1, R25.1
REF_ELEC_CON: JP16.23, R25.2
SRB1: JP6.2, JP8.2; also elsewhere on the board
SRB2: JP7.3; also elsewhere on the board

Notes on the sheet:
Electrode Connector
Stimulus-Response Buffer (SRB)
Bias
Released under the CERN Open Hardware License v.1.2
Copyright 2013-2020 Adam Feuer
Input Filtering
(This side to ADS1299 inputs)
(This side to electrode connector)

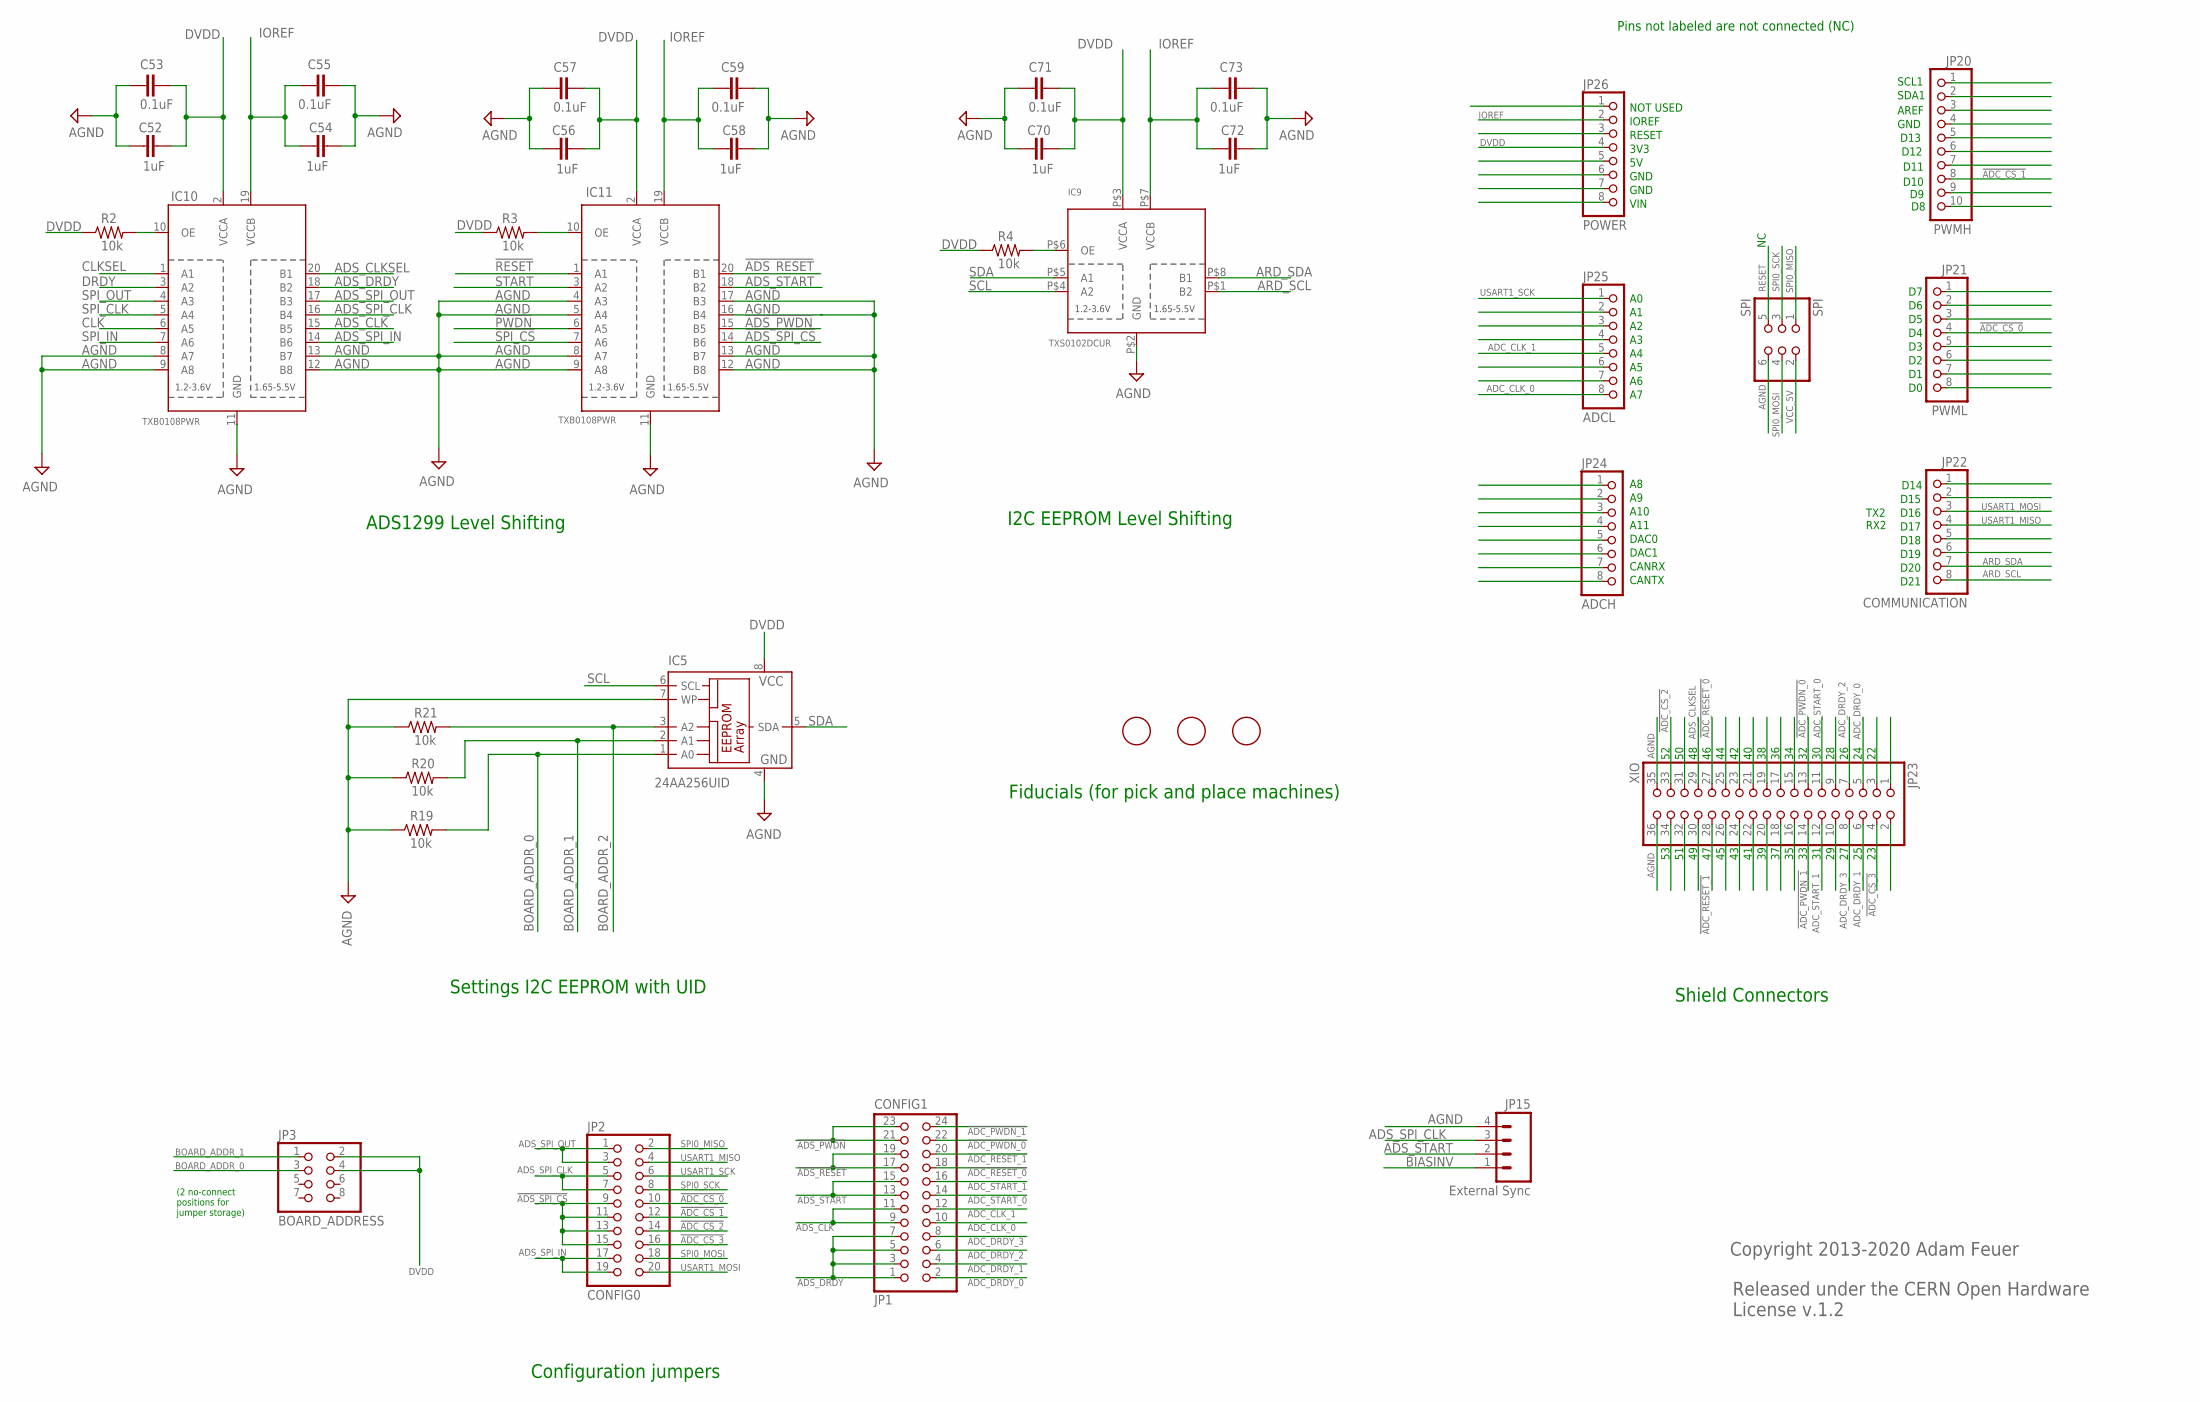
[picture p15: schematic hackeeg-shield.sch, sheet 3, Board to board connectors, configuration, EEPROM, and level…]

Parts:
C52, C54, C56, C58, C70, C72: 1uF; 0603-CAP
C53, C55, C57, C59, C71, C73: 0.1uF; 0603-CAP
IC5: 24AA256UID; SO-08
IC9: TXS0102DCUR; VFSOP-8
IC10, IC11: TXB0108PWR; TSSOP20
JP1: CONFIG1; 2X12
JP2: CONFIG0; 2X10
JP3: BOARD_ADDRESS; 2X04
JP15: External Sync; JST-4-PTH
JP20: PWMH; 1X10
JP21: PWML; 1X08
JP22: COMMUNICATION; 1X08
JP23: XIO; 2X18
JP24: ADCH; 1X08
JP25: ADCL; 1X08
JP26: POWER; 1X08
R2, R3, R4, R19, R20, R21: 10k; 0603-RES
SPI: SPI; 2X03
U$2, U$5, U$6: FIDUCIAL; FIDUCIAL_1MM

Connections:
!ADC_CS_0: JP2.10, JP21.4
!ADC_CS_1: JP2.12, JP20.8
!ADC_CS_2: JP2.14, JP23.33
!ADC_CS_3: JP2.16, JP23.4
!ADC_PWDN_0: JP1.22, JP23.13
!ADC_PWDN_1: JP1.24, JP23.14
!ADC_RESET_0: JP1.18, JP23.27
!ADC_RESET_1: JP1.20, JP23.28
!ADS_PWDN: IC11.15 (B5), JP1.21, JP1.23
!ADS_RESET: IC11.20 (B1), JP1.17, JP1.19
!ADS_SPI_CS: IC11.14 (B6), JP2.9, JP2.11, JP2.13, JP2.15
!PWDN: IC11.6 (A5); also elsewhere on the board
!RESET: IC11.1 (A1); also elsewhere on the board
!SPI_CS: IC11.7 (A6); also elsewhere on the board
ADC_CLK_0: JP1.10, JP25.8
ADC_CLK_1: JP1.12, JP25.5
ADC_DRDY_0: JP1.2, JP23.5
ADC_DRDY_1: JP1.4, JP23.6
ADC_DRDY_2: JP1.6, JP23.7
ADC_DRDY_3: JP1.8, JP23.8
ADC_START_0: JP1.14, JP23.11
ADC_START_1: JP1.16, JP23.12
ADS_CLK: IC10.15 (B5), JP1.9, JP1.11
ADS_CLKSEL: IC10.20 (B1), JP23.29
ADS_DRDY: IC10.18 (B2), JP1.1, JP1.3, JP1.5, JP1.7
ADS_SPI_CLK: IC10.16 (B4), JP2.5, JP2.7, JP15.3
ADS_SPI_IN: IC10.14 (B6), JP2.17, JP2.19
ADS_SPI_OUT: IC10.17 (B3), JP2.1, JP2.3
ADS_START: IC11.18 (B2), JP1.13, JP1.15, JP15.2
AGND: C52.1, C53.1, C54.1, C55.1, C56.1, C57.1, C58.1, C59.1, C70.1, C71.1, C72.1, C73.1, IC5.4 (GND), IC5.7 (WP), IC9.P$2 (GND), IC10.8 (A7), IC10.9 (A8), IC10.11 (GND), IC10.12 (B8), IC10.13 (B7), IC11.4 (A3), IC11.5 (A4), IC11.8 (A7), IC11.9 (A8), IC11.11 (GND), IC11.12 (B8), IC11.13 (B7), IC11.16 (B4), IC11.17 (B3), JP15.4, JP23.35, JP23.36, R19.1, R20.1, R21.1, SPI.6; also elsewhere on the board
ARD_SCL: IC9.P$1 (B2), JP22.8
ARD_SDA: IC9.P$8 (B1), JP22.7
BIASINV: JP15.1; also elsewhere on the board
BOARD_ADDR_0: IC5.1 (A0), JP3.3, R19.2; also elsewhere on the board
BOARD_ADDR_1: IC5.2 (A1), JP3.1, R20.2; also elsewhere on the board
BOARD_ADDR_2: IC5.3 (A2), R21.2; also elsewhere on the board
CLK: IC10.6 (A5); also elsewhere on the board
CLKSEL: IC10.1 (A1); also elsewhere on the board
DRDY: IC10.3 (A2); also elsewhere on the board
DVDD: C52.2, C53.2, C56.2, C57.2, C70.2, C71.2, IC5.8 (VCC), IC9.P$3 (VCCA), IC10.2 (VCCA), IC11.2 (VCCA), JP3.2, JP3.4, JP26.4, R2.1, R3.1, R4.1; also elsewhere on the board
IOREF: C54.2, C55.2, C58.2, C59.2, C72.2, C73.2, IC9.P$7 (VCCB), IC10.19 (VCCB), IC11.19 (VCCB), JP26.2
unnamed: IC9.P$6 (OE), R4.2
unnamed: IC10.10 (OE), R2.2
unnamed: IC11.10 (OE), R3.2
RESET: SPI.5
SCL: IC5.6 (SCL), IC9.P$4 (A2)
SDA: IC5.5 (SDA), IC9.P$5 (A1)
SPI0_MISO: JP2.2, SPI.1
SPI0_MOSI: JP2.18, SPI.4
SPI0_SCK: JP2.8, SPI.3
SPI_CLK: IC10.5 (A4); also elsewhere on the board
SPI_IN: IC10.7 (A6); also elsewhere on the board
SPI_OUT: IC10.4 (A3); also elsewhere on the board
START: IC11.3 (A2); also elsewhere on the board
USART1_MISO: JP2.4, JP22.4
USART1_MOSI: JP2.20, JP22.3
USART1_SCK: JP2.6, JP25.1
VCC_5V: SPI.2; also elsewhere on the board

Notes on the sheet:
Configuration jumpers
ADS1299 Level Shifting
Settings I2C EEPROM with UID
(2 no-connect positions for jumper storage)
Released under the CERN Open Hardware License v.1.2
Copyright 2013-2020 Adam Feuer
Shield Connectors
SCL1
SDA1
AREF
GND
D14
D15
D16
D17
D18
D19
D20
D21
A10
A11
DAC0
DAC1
CANRX
CANTX
NOT USED
IOREF
RESET
3V3
VIN
Fiducials (for pick and place machines)
TX2
RX2
I2C EEPROM Level Shifting
Pins not labeled are not connected (NC)
D13
D12
D11
D10

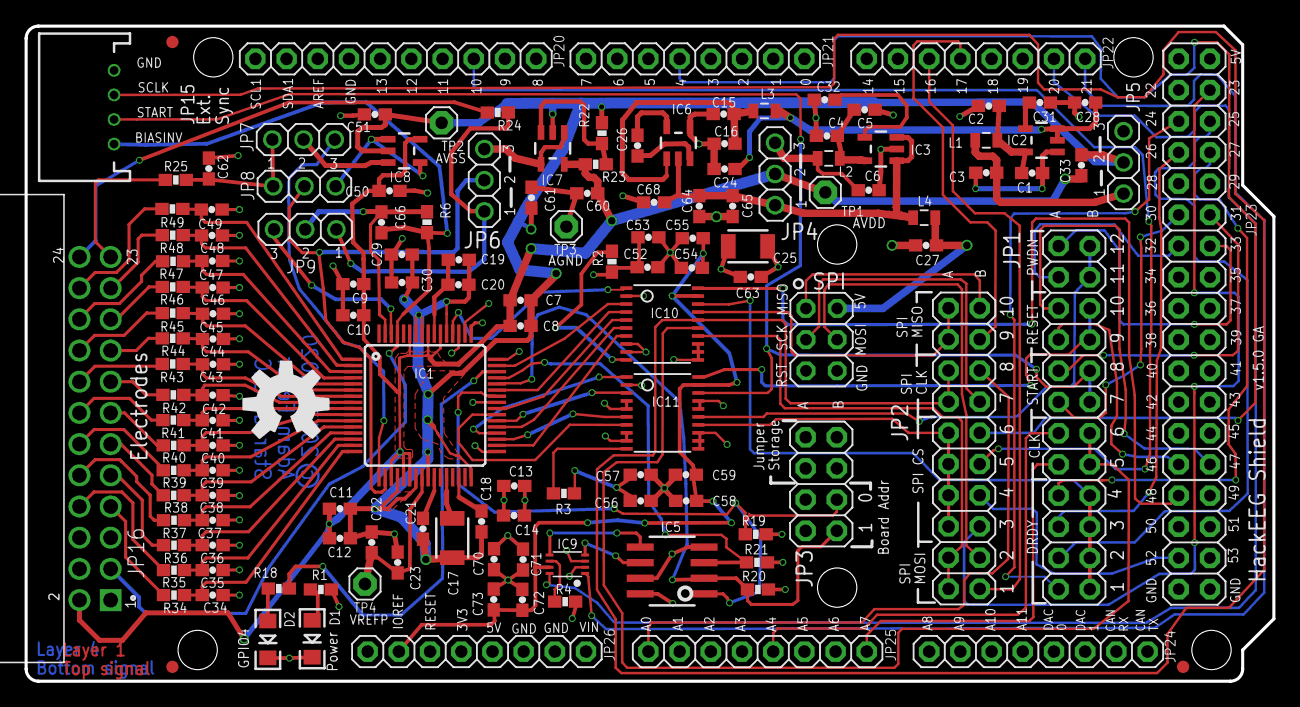
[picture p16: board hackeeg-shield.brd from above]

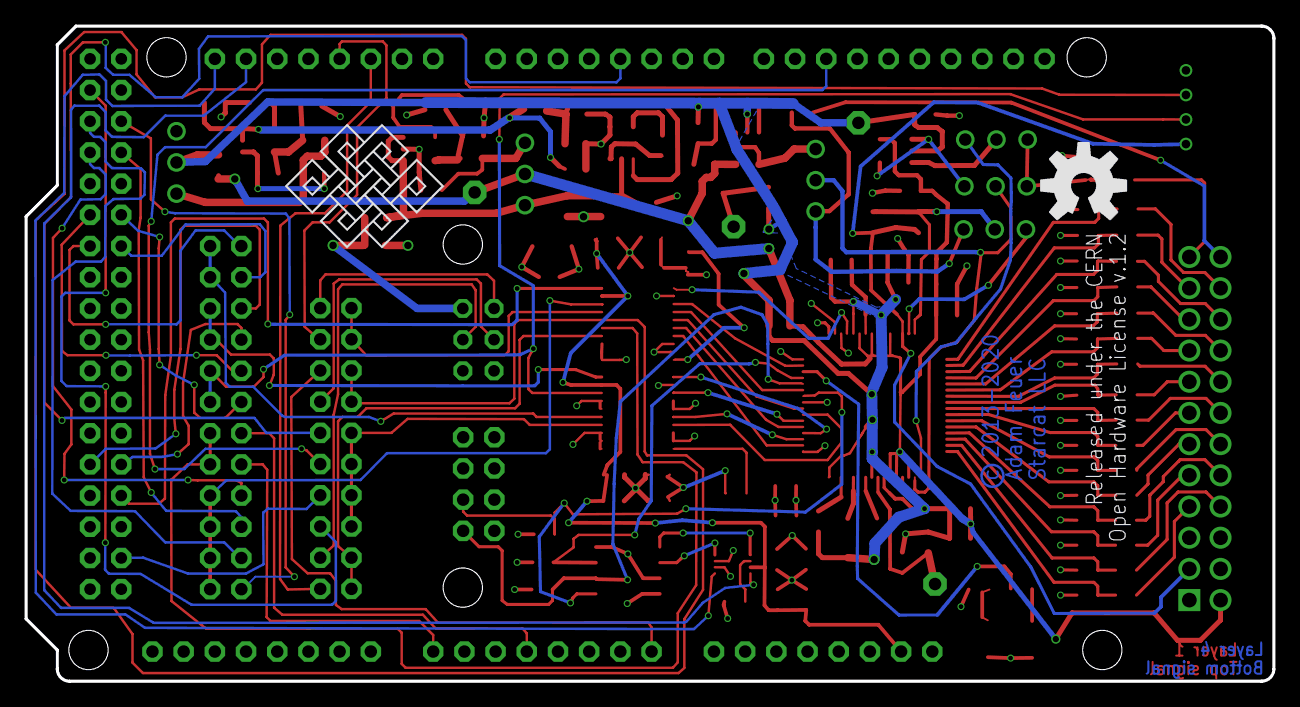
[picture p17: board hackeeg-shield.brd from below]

Board: 4 copper layers, 101.6 x 53.3 mm, 145 parts (2 on the bottom side), 122 nets.

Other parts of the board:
U$1, U$4: OSHW-LOGO-L
U$7: ENDLESSKNOT-MEDIUM

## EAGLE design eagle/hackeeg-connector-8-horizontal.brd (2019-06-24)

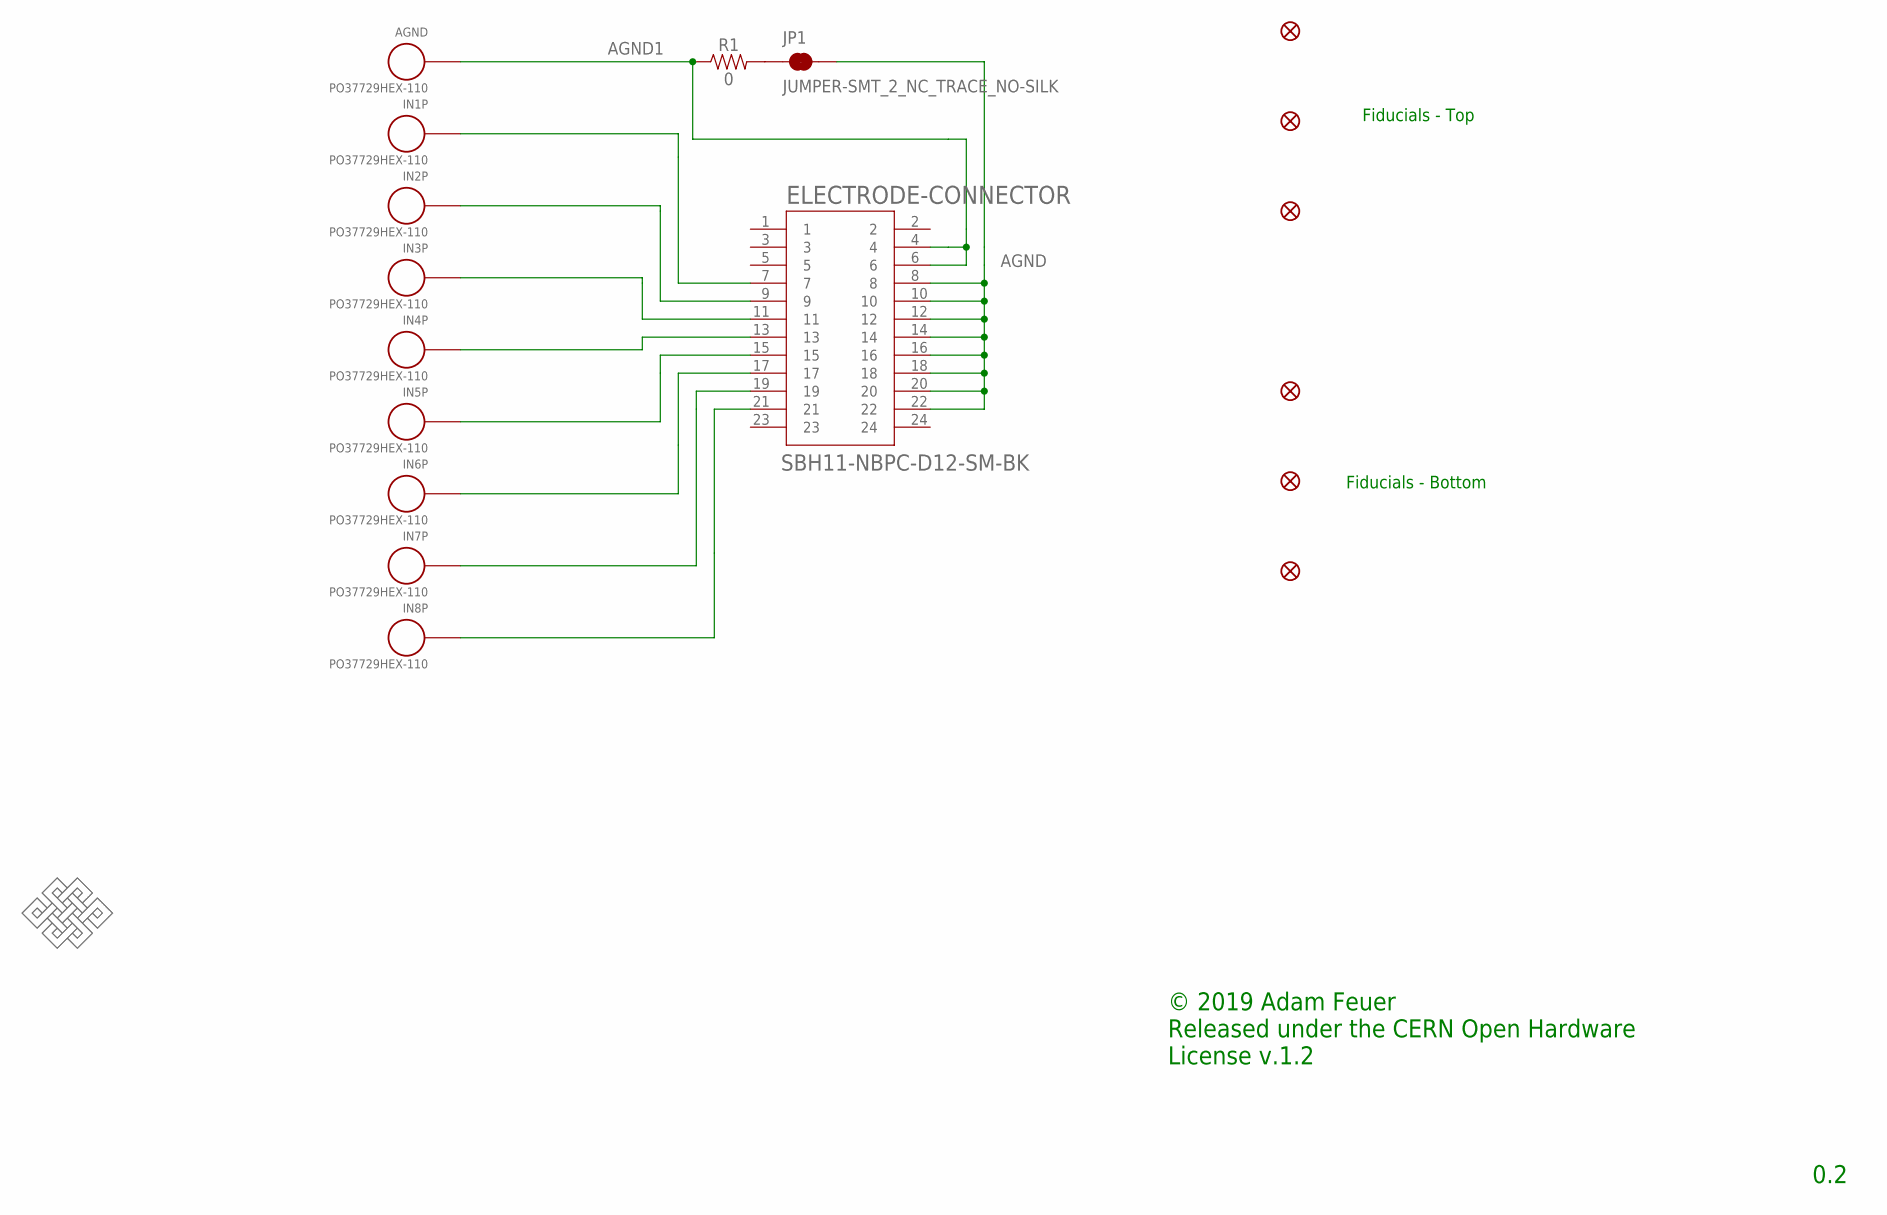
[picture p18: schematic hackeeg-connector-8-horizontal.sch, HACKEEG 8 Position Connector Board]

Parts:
AGND: PO37729HEX-110; HEX-110
ELECTRODE-CONNECTOR: SBH11-NBPC-D12-SM-BK; SULLINS_SBH11-NBPC-D12-SM-BK
FD1, FD2, FD3, FD4, FD5, FD6: FIDUCIAL1X2; FIDUCIAL-1X2
IN1P, IN2P, IN3P, IN4P, IN5P, IN6P, IN7P, IN8P: PO37729HEX-110; HEX-110
JP1: JUMPER-SMT_2_NC_TRACE_NO-SILK; SMT-JUMPER_2_NC_TRACE_NO-SILK
R1: 0; 0603
U$1: ENDLESSKNOTENDLESSKNOT-MEDIUM; ENDLESSKNOT-MEDIUM

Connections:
AGND: ELECTRODE-CONNECTOR.8, ELECTRODE-CONNECTOR.10, ELECTRODE-CONNECTOR.12, ELECTRODE-CONNECTOR.14, ELECTRODE-CONNECTOR.16, ELECTRODE-CONNECTOR.18, ELECTRODE-CONNECTOR.20, ELECTRODE-CONNECTOR.22, JP1.2
AGND1: AGND.SIGNAL, ELECTRODE-CONNECTOR.4, ELECTRODE-CONNECTOR.6, R1.1
unnamed: ELECTRODE-CONNECTOR.7, IN1P.SIGNAL
unnamed: ELECTRODE-CONNECTOR.9, IN2P.SIGNAL
unnamed: ELECTRODE-CONNECTOR.11, IN3P.SIGNAL
unnamed: ELECTRODE-CONNECTOR.13, IN4P.SIGNAL
unnamed: ELECTRODE-CONNECTOR.15, IN5P.SIGNAL
unnamed: ELECTRODE-CONNECTOR.17, IN6P.SIGNAL
unnamed: ELECTRODE-CONNECTOR.19, IN7P.SIGNAL
unnamed: ELECTRODE-CONNECTOR.21, IN8P.SIGNAL
unnamed: JP1.1, R1.2

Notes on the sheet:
Fiducials - Top
Fiducials - Bottom
© 2019 Adam Feuer Released under the CERN Open Hardware License v.1.2
0.2

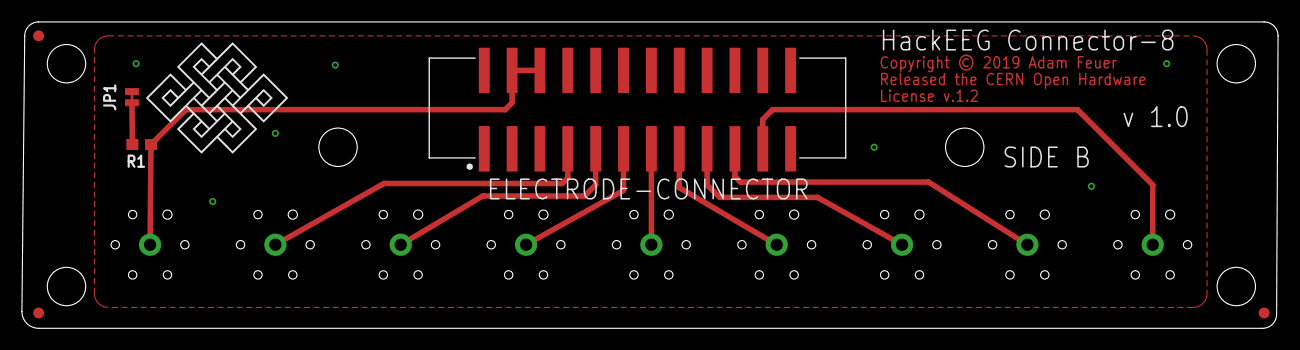
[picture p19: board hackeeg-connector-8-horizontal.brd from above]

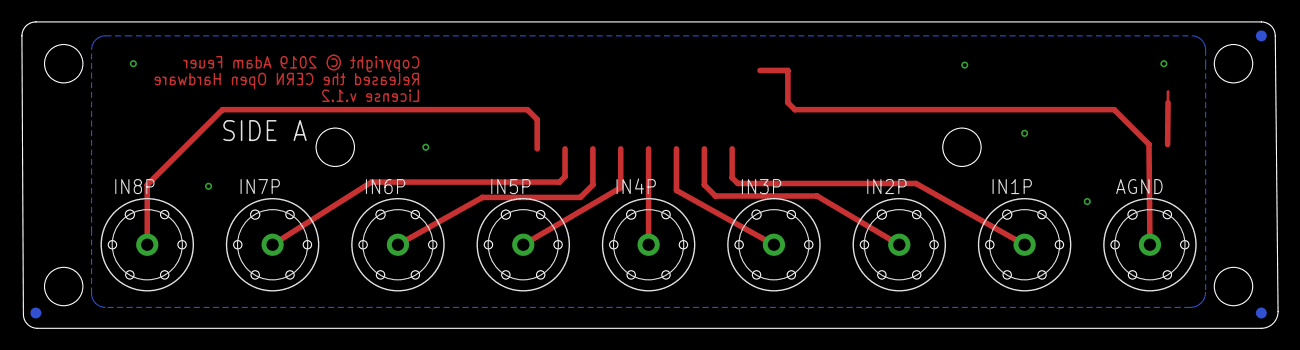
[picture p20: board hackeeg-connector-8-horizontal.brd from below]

Board: 2 copper layers, 114.6 x 27.9 mm, 19 parts (12 on the bottom side), 11 nets.

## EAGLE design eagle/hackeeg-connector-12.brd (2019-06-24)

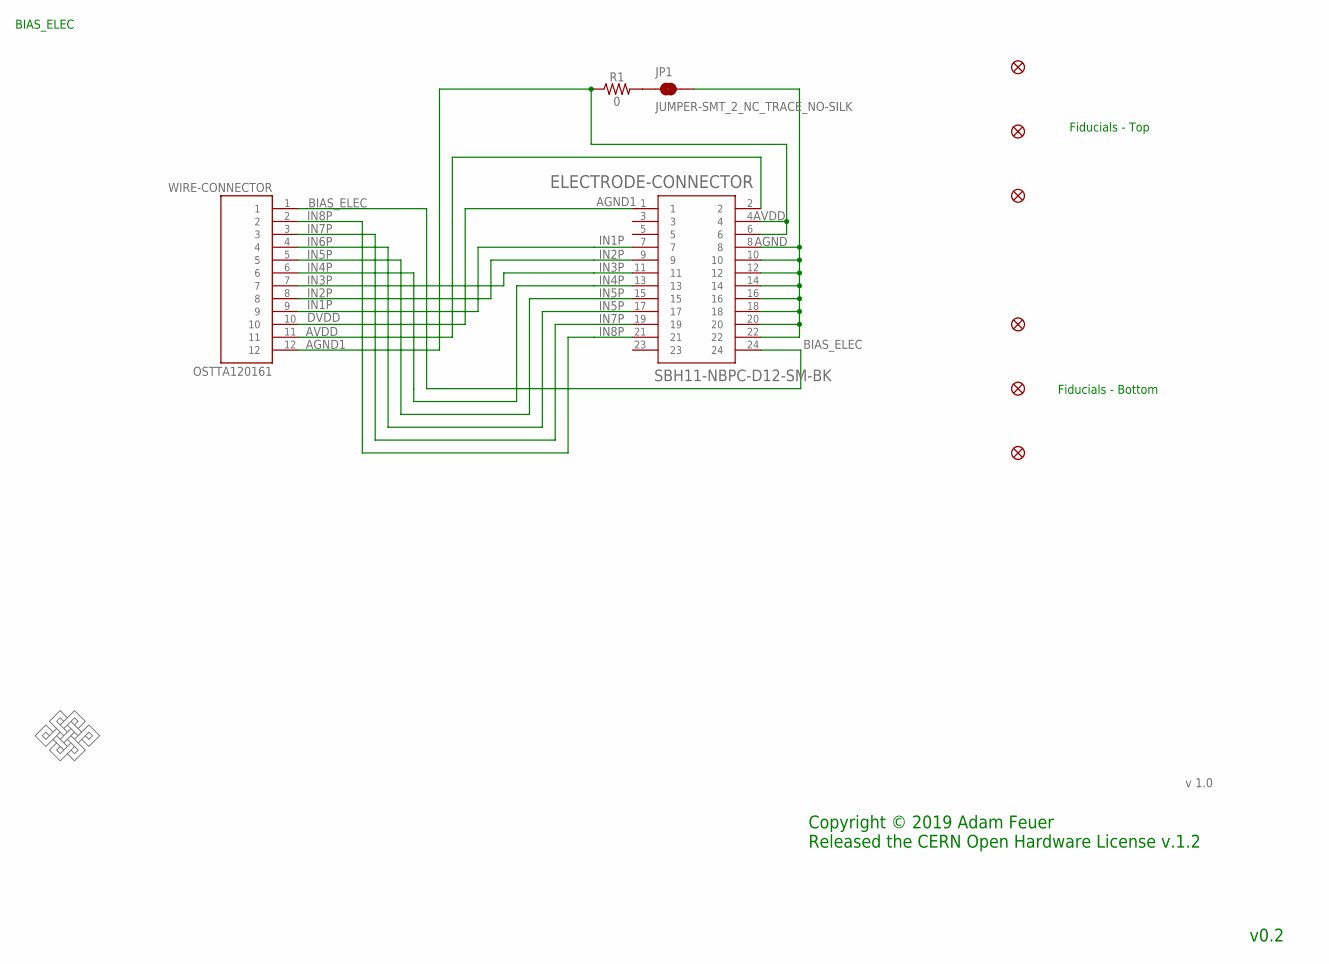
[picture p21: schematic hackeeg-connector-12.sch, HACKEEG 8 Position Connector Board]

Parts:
ELECTRODE-CONNECTOR: SBH11-NBPC-D12-SM-BK; SULLINS_SBH11-NBPC-D12-SM-BK
FD1, FD2, FD3, FD4, FD5, FD6: FIDUCIAL1X2; FIDUCIAL-1X2
JP1: JUMPER-SMT_2_NC_TRACE_NO-SILK; SMT-JUMPER_2_NC_TRACE_NO-SILK
R1: 0; 0603
U$1: ENDLESSKNOTENDLESSKNOT-MEDIUM; ENDLESSKNOT-MEDIUM
WIRE-CONNECTOR: OSTTA120161; ONSHORE_OSTTA120161

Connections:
AGND: ELECTRODE-CONNECTOR.8, ELECTRODE-CONNECTOR.10, ELECTRODE-CONNECTOR.12, ELECTRODE-CONNECTOR.14, ELECTRODE-CONNECTOR.16, ELECTRODE-CONNECTOR.18, ELECTRODE-CONNECTOR.20, ELECTRODE-CONNECTOR.22, JP1.2
AGND1: ELECTRODE-CONNECTOR.4, ELECTRODE-CONNECTOR.6, R1.1, WIRE-CONNECTOR.12
AVDD: ELECTRODE-CONNECTOR.2, WIRE-CONNECTOR.11
BIAS_ELEC: ELECTRODE-CONNECTOR.24, WIRE-CONNECTOR.1
DVDD: ELECTRODE-CONNECTOR.1, WIRE-CONNECTOR.10
IN1P: ELECTRODE-CONNECTOR.7, WIRE-CONNECTOR.9
IN2P: ELECTRODE-CONNECTOR.9, WIRE-CONNECTOR.8
IN3P: ELECTRODE-CONNECTOR.11, WIRE-CONNECTOR.7
IN4P: ELECTRODE-CONNECTOR.13, WIRE-CONNECTOR.6
IN5P: ELECTRODE-CONNECTOR.15, WIRE-CONNECTOR.5
IN6P: ELECTRODE-CONNECTOR.17, WIRE-CONNECTOR.4
IN7P: ELECTRODE-CONNECTOR.19, WIRE-CONNECTOR.3
IN8P: ELECTRODE-CONNECTOR.21, WIRE-CONNECTOR.2
unnamed: JP1.1, R1.2

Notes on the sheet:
Fiducials - Top
Fiducials - Bottom
BIAS_ELEC
IN1P
IN2P
IN3P
IN4P
IN5P
IN7P
IN8P
AGND1
AVDD
v 1.0
v0.2
Copyright © 2019 Adam Feuer Released the CERN Open Hardware License v.1.2



Board: 2 copper layers, 77.7 x 27.9 mm, 11 parts (4 on the bottom side), 14 nets.

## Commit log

2013-11-05 initial addition, based on ADS1298-breakout
    [ADS1299-shield.brd, ADS1299-shield.sch]
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2013-11-06 schematic work - power supplies and decoupling done; updated ADS1299 library symbol to better organize pinouts; minor updates to power supply libraries
    [ADS1299-shield.brd, ADS1299-shield.sch]
2013-11-06 updated ads1299 library to have NAME and VALUE; improved power supply section, including supply-select jumpers
    [ADS1299-shield.brd, ADS1299-shield.sch]
2013-11-07 input filtering section done
    [ADS1299-shield.brd, ADS1299-shield.sch]
2013-11-08 configuration jumpers added but not done; EEPROM in and finished; level shifters finished
    [ADS1299-shield.brd, ADS1299-shield.sch]
2013-11-09 renamed v1.0/ directory to eagle/
    [ADS1299-shield.brd, ADS1299-shield.sch]
2013-11-09 configuration jumpers almost complete - board address in, and all configurable digital signals in
    [ADS1299-shield.brd, ADS1299-shield.sch]
2013-11-09 added 2x15 header to header library; used it for electrode connector, which is finished
    [ADS1299-shield.brd, ADS1299-shield.sch]
2013-11-09 SRB and Bias op-amps in; REF_ELEC and BIAS_ELEC on electrode connector
    [ADS1299-shield.brd, ADS1299-shield.sch]
2013-11-10 corrected mixed up N and P pins in OPA375 library; some cleanup
    [ADS1299-shield.brd, ADS1299-shield.sch]
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2013-11-11 board outline in, copied from Arduino Due reference design; holes in; connectors in both schematic and board, but not connected in schematic
    [ADS1299-shield.brd, ADS1299-shield.sch]
2013-11-11 all components on board, but not arranged well; connectors not hooked up
    [ADS1299-shield.brd, ADS1299-shield.sch]
2013-11-11 added level shifting for EEPROM SDA and SCL; added some wires for labeling shield connectors (SPI and XIO not done)
    [ADS1299-shield.brd, ADS1299-shield.sch]
2013-11-11 added wires for labeling SPI and XIO connectors
    [ADS1299-shield.brd, ADS1299-shield.sch]
2013-11-11 wires and labels added for SPI and XIO connectors
    [ADS1299-shield.brd, ADS1299-shield.sch]
2013-11-11 added connections for ADC SPI IN, OUT, CLK; and ADC_CLK
    [ADS1299-shield.brd, ADS1299-shield.sch]
2013-11-12 all necessary signals routed to shield connectors; schematic passes ERC
    [ADS1299-shield.brd, ADS1299-shield.sch]
2013-11-13 added test points for power; added fiducials; partially grouped AIN block passives, EEPROM resistors, and level shifter decoupling caps
    [ADS1299-shield.brd, ADS1299-shield.sch]
2013-11-13 grouped positive and negative power components
    [ADS1299-shield.brd, ADS1299-shield.sch]
2013-11-13 arranged components by function - AIN filters, ADC and decoupling, power, SRB, Bias, level shifters, EEPROM
    [ADS1299-shield.brd, ADS1299-shield.sch]
2013-11-14 fixed errors in AIN block; some airwires; level shifter output enable is now connected and held high
    [ADS1299-shield.brd, ADS1299-shield.sch]
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2013-11-19 fixed DRC errors related to top-side polygons
    [ADS1299-shield.brd]
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2013-11-20 many minor improvements - more mitering polygons, traces enlarged from 6mil to 8mil, clearances improved where possible
    [ADS1299-shield.brd]
2013-11-21 updated headers in SmartPrj to have smaller pads; moved traces away from edge of board; minor clearance improvements; documentation labels for configuration jumpers partly done
    [ADS1299-shield.brd, ADS1299-shield.sch]
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2013-11-21 fixed problem with test point 2
    [ADS1299-shield.brd, ADS1299-shield.sch]
2013-11-21 minor clearance and legend improvements
    [ADS1299-shield.brd]
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2013-11-23 widened traces; improved jumper clearance for JP5
    [ADS1299-shield.brd]
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2013-11-25 fixed many errors found by rechecking ADS1299 Eval Board schematic. Rerouted board. Passes ERC and DRC.
    [ADS1299-shield.brd, ADS1299-shield.sch]
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2013-11-25 updated cam job to not output tDocu; fixed problems with some top polygons
    [ADS1299-shield.brd]
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2013-11-25 correcting mistakes in BOM
    [ADS1299-shield-bom.xlsx]
2013-12-28 fixes to schematic and board - created VCC_5V_FILTERED net to correct current draw problem; changed inductors to 0805 to fix current flow problem
    [ADS1299-shield-bom.xlsx, ADS1299-shield.brd, ADS1299-shield.sch]
2013-12-28 rotated XIO connector to correct orientation
    [ADS1299-shield.brd]
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2013-12-29 moved electrode connector up a bit so it doesn't hang over the bottom edge so much; also moved sync connector up to top edge
    [ADS1299-shield.brd]
2013-12-29 minor trace clearance change
    [ADS1299-shield.brd]
2013-12-29 minor updates to trace clearances; moved logos on bottom of board so the don't cover the copyright
    [ADS1299-shield.brd, ADS1299-shield.sch]
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2013-12-31 changed serial EEPROM to use I2C port SDA/SCL instead of SDA1/SCL1 due to lack of pull up resistors and Mega2560 incompatibility (Mega2560 has pull-ups on those pins already; Due doesn't)
    [ADS1299-shield.brd, ADS1299-shield.sch]
2014-01-01 renamed TPS32xx library to TPS732xx; fixed incorrect pin mapping
    [ADS1299-shield.brd, ADS1299-shield.sch]
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2014-01-03 fixed fiducial locations - 2 share X coords; 2 share Y coords
    [hackeeg-shield.brd]
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2014-01-07 updates to fix keepout errors; minor silkscreen improvements
    [hackeeg-shield.brd, hackeeg-shield.sch]
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2014-01-09 updated BOM to used JST through-hole connector for sync; fixed bottomlayer trace widths and routing
    [hackeeg-shield.brd]
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2014-01-16 fixed silkscreen pin label bug - DAC0/1, CAN RX/TX
    [hackeeg-shield.brd]
2014-01-21 fixed Analog Input filter bug; added BIASINV signal to electrode connector and to unused power connector pin, with solder jumper; improved trace clearances
    [hackeeg-shield.brd, hackeeg-shield.sch]
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2014-01-25 changed solder mask (cream) stop to 1mil so stencils cut correctly using gerber2graphtec & graphtec cameo cutter
    [hackeeg-shield.brd]
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2014-01-26 added circular restrict polygons on AGND and DVDD layers, surrounding mounting holes - to avoid problems with Advanced Circuits plating the holes and causing short circuits
    [hackeeg-shield.brd]
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2014-01-28 changed inner layer (AGND and DVDD) polygon isolate clearance to 12 mils (from 0)
    [hackeeg-shield.brd, hackeeg-shield.sch]
2014-01-28 updated cam file to have better clearances; changed routing to avoid congestion and close traces on right edge of board toop and bottom
    [hackeeg-shield.brd]
2014-01-28 changed rest-rings to min 12mil and fixed all DRC errors
    [hackeeg-shield.brd]
2014-01-29 updated layer AGND and DVDD text to have larger widths and enclosing cutout box to prevent clearance errors
    [hackeeg-shield.brd]
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2014-02-04 fixed problem with jumper legend lines being on bottom of board - moved to top
    [hackeeg-shield.brd]
2014-02-06 moved SRB2 bottom trace so it doesn't pass under electrode inputs
    [hackeeg-shield.brd]
2014-02-07 improving trace clearances
    [hackeeg-shield.brd]
2014-02-16 fixed schematic and board bug - opamp OPA376 VDD and VSS pins were reversed; updated schematic and board version to 1.3.1
    [hackeeg-shield.brd, hackeeg-shield.sch]
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2014-02-17 minor via and trace clearance improvements
    [hackeeg-shield.brd]
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2014-02-17 changed copper text spacing on Layer 4 (bottom) to fix hole-text clearance
    [hackeeg-shield.brd]
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2016-06-06 fix for bipolar mode 2.25x problem (VREFN-AVSS)
    - disconnected VREFN from AGND
    - connected VREFN to AVSS
    - rerouted traces
    - minor labeling changes - labeled all board to board connectors
    - bumped version to 1.4.0
    [hackeeg-shield.brd, hackeeg-shield.sch]
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2016-08-29 fixed problem with BIASOUT/BIASINV
    - for common mode noise rejection
    [hackeeg-shield.brd, hackeeg-shield.sch]
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2016-09-22 minor routing adjustments
    - for JP9 clearance
    [hackeeg-shield.brd]
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2018-09-24 removed ground planes
    - to reduce noise
    [hackeeg-connector-8.brd]
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2018-09-25 Revert "removed ground planes"
    This reverts commit f4ca484e04cfc3e6669577150c464fbf194e8d2b.
    [hackeeg-connector-8.brd]
2018-09-25 connected IN1-8N to AGND
    - for cable noise reduction
    [hackeeg-connector-8.brd, hackeeg-connector-8.sch]
2018-09-25 connected IN1-8N to ground
    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
    [hackeeg-connector-32.sch]
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2018-12-01 added two additional mounting holes
    - to prevent bending problems.
    [hackeeg-connector-8.brd]
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2019-04-16 corrected connector spacing and made board smaller
    - all connectors are now evenly spaced
    [hackeeg-connector-8.brd, hackeeg-connector-8.sch]
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2019-04-19 fixed side B AGND plane; updated CAM job
    - updated CAM job for Eagle 9.1.2
    [hackeeg-connector-8.brd]
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2019-04-24 replaced OSTTA120161B with OSTTA120161 library
    [hackeeg-connector-12.brd, hackeeg-connector-12.sch]
2019-05-02 replaced electrode connector with new connector
    - On Shore Technologies male shrouded header OS302-R241.lbr
    - to match cable connectors
    [hackeeg-shield.brd, hackeeg-shield.sch]
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

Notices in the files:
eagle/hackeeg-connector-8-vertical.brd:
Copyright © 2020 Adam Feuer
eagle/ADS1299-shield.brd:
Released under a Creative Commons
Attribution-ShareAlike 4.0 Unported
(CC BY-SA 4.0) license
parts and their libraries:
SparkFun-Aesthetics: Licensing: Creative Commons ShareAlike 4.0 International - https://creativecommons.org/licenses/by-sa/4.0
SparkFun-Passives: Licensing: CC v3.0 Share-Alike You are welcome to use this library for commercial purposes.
